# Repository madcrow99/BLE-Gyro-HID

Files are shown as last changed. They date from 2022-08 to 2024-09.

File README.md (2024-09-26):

# BLE-Gyro-HID

This project is to create a low-cost human interface device (HID) that enables people with motor impairments to control phones and computers. Basically, a mouse that requires very limited head movements to operate.
please see this repository for how to game and control phones using only eye gaze https://github.com/madcrow99/windows-eye-control-of-external-devices.git

The device uses a gyroscope mounted to an earpiece to track head movements (very little movement required) and move a mouse pointer accordingly. The device has 4 optional switch / button inputs (3.5mm headphone jack) for use with any switches that the user can control.

left: works the same as the left click button on a regular mouse

right: works the same as the right click button on a regular mouse 

scroll: tap to scroll down and long press to scroll up

dwell: tap to to toggle dwell clicking on and off. Dwell clicking is where the device will left click/tap when the pointer is stationary for a specified time. Being able to turn this feature on and off really helps the user from going crazy when the mouse constantly clicks.





The device uses an Adafruit Feather Express nRF52840 and an IMU module to act as a Bluetooth low energy mouse. Please see the bill of materials for details. The case and gyro cover are 3d printed. The STL and STEP files ae included. The Nordic nRF52840 is an amazing device and the Adafruit implementation of it is awesome. Thanks Adafruit for the wonderfully easy to use libraries!

An instruction manual for building the device is included.

The software has to be uploaded to the nRF52840. Platformio is recommended. Here is a link to the setup instructions:
https://platformio.org/install/ide?install=vscode

An Android App that performs swipe gestures when clicked can be found here
https://github.com/madcrow99/AndroidMousePointerSwipeGestures
This is quite helpful for navigating an android device while dwell cicking.

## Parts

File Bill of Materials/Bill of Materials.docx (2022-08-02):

Bill of Materials

The majority of the parts come from Adafruit:

https://www.adafruit.com/

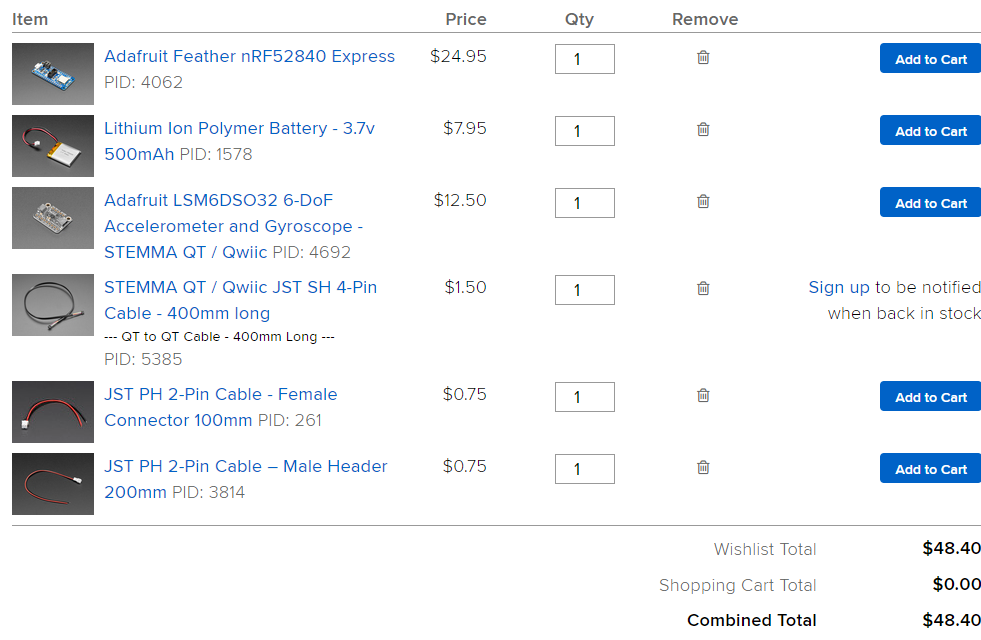
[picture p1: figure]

The parts below are from Amazon but can be purchased elsewhere. Digikey is a great source.

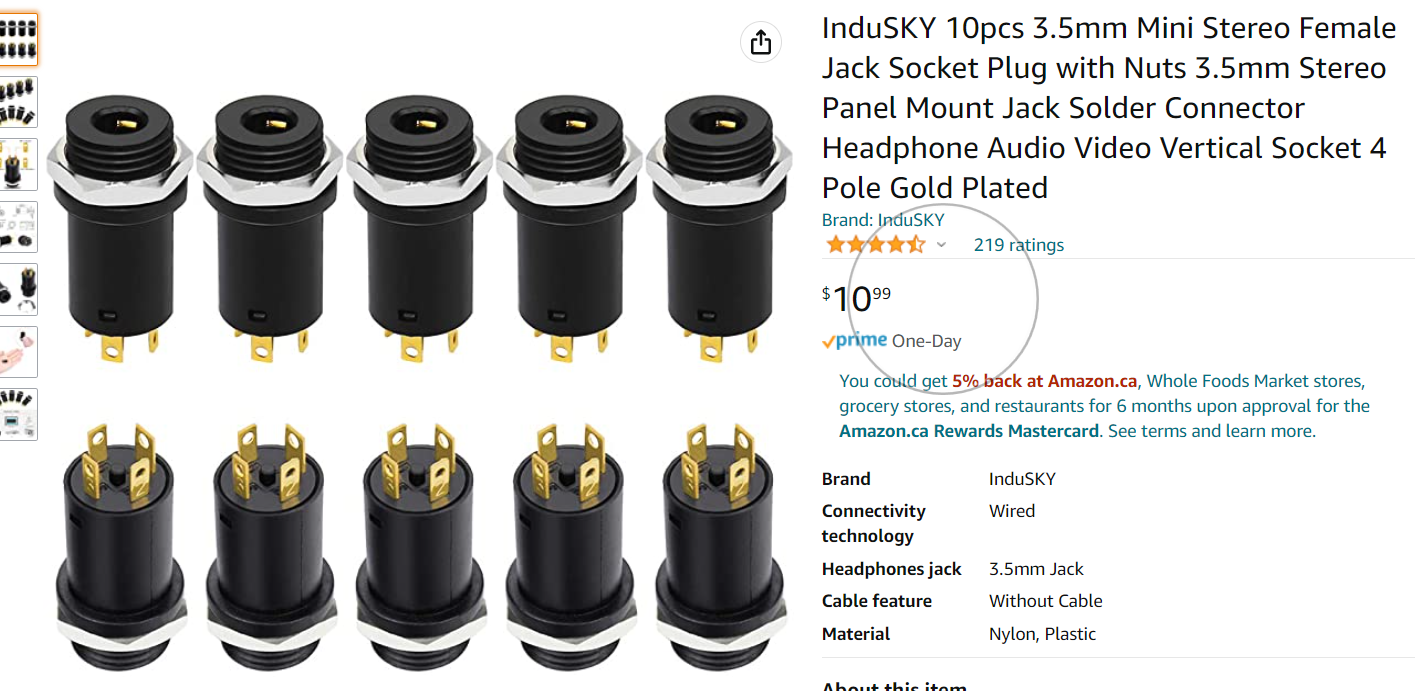
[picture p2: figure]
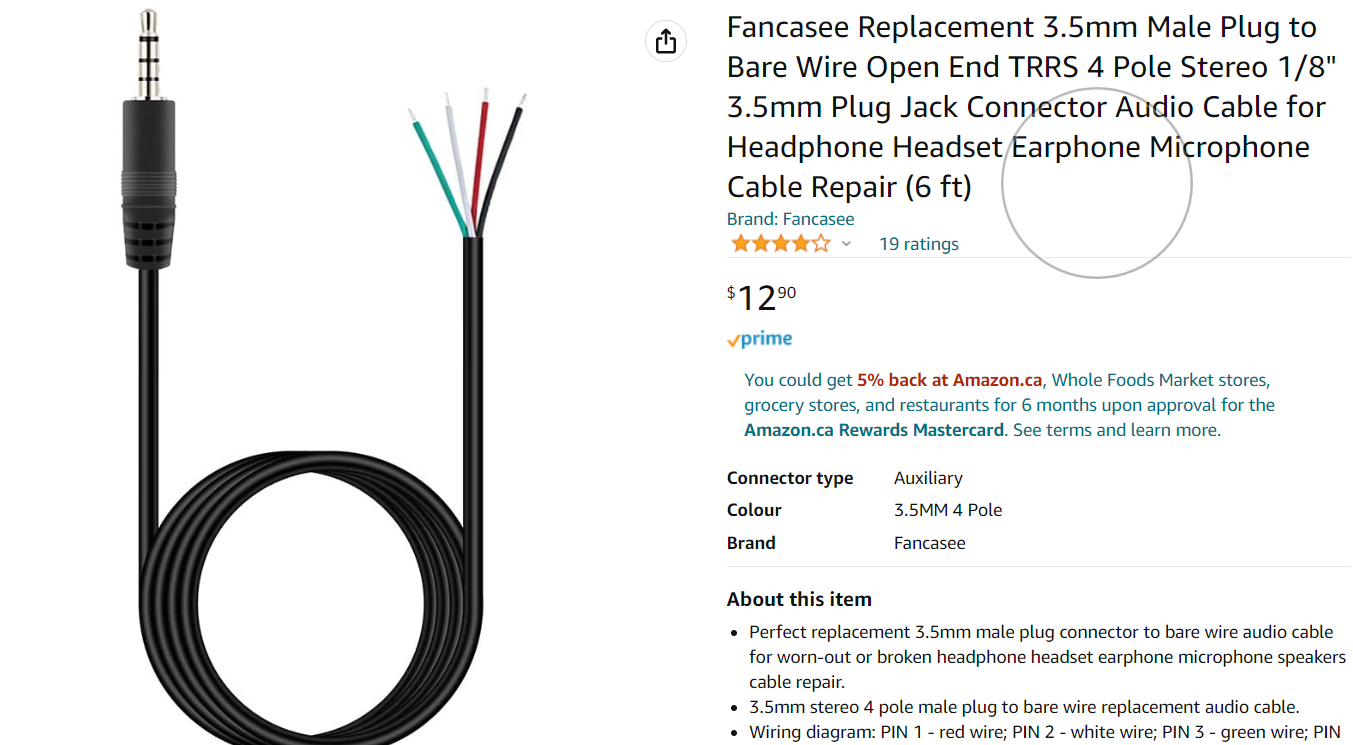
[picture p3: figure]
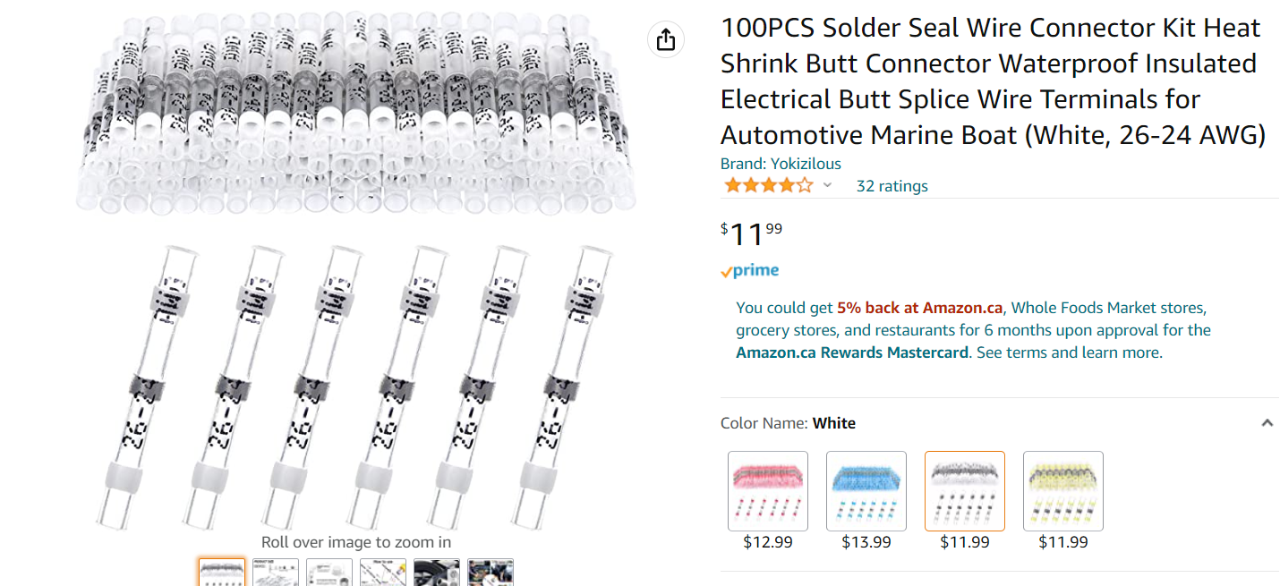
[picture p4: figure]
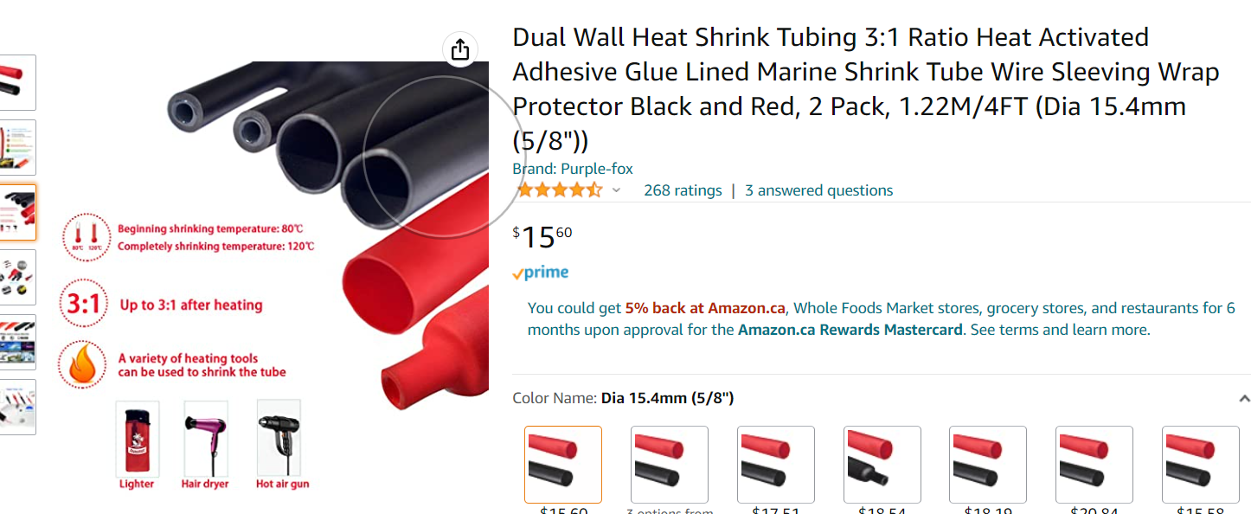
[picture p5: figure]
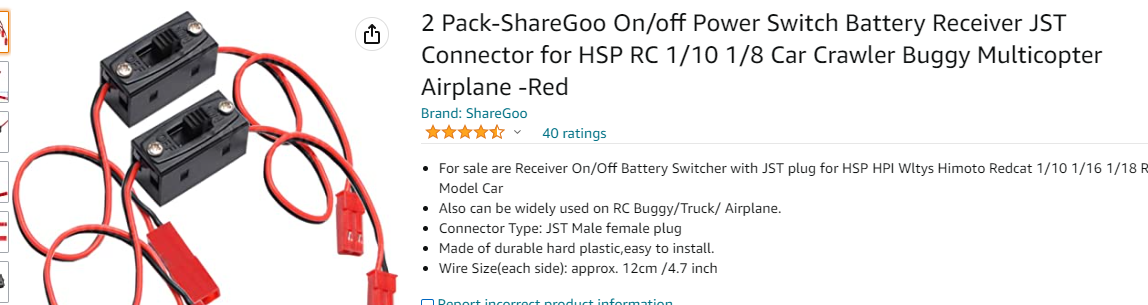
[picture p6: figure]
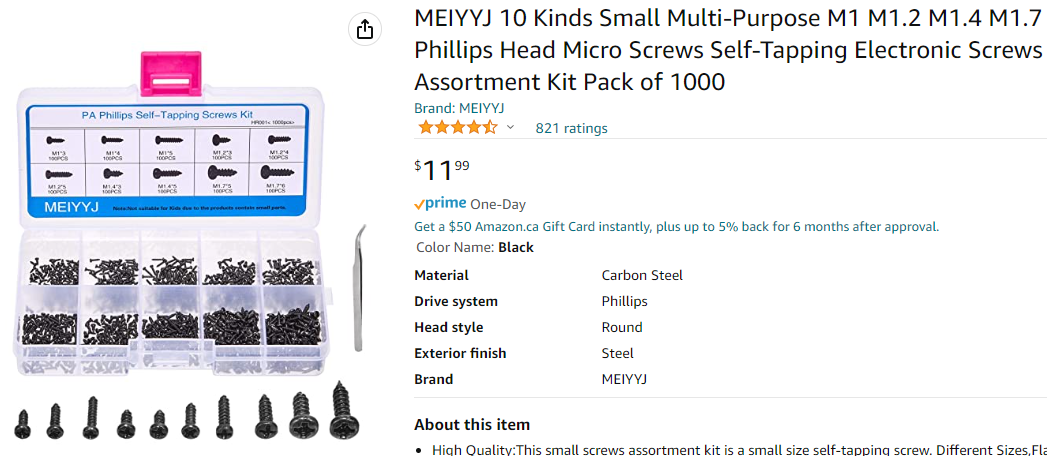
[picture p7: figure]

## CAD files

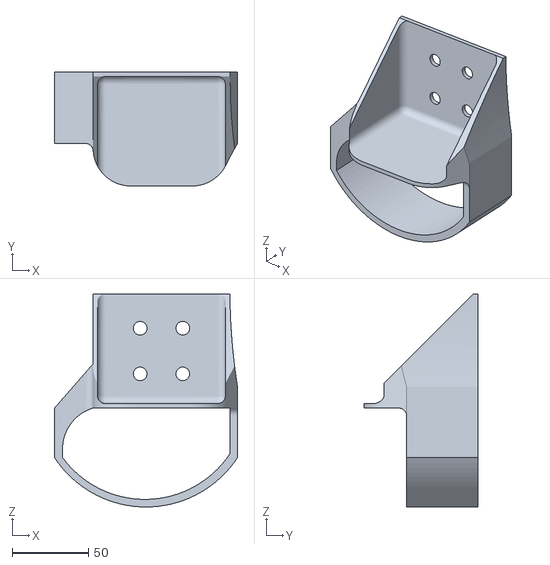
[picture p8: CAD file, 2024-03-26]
3D print STL files/Hand Button Mount Left.stl
120.3 x 75.0 x 140.0

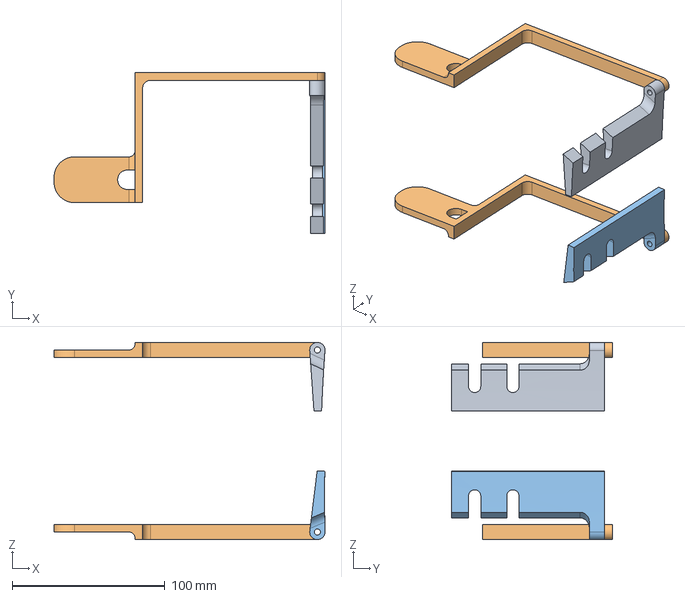
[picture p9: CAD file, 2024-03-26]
CAD STEP Files/Head Button Mount.step
177.2 x 105.0 x 129.0 mm

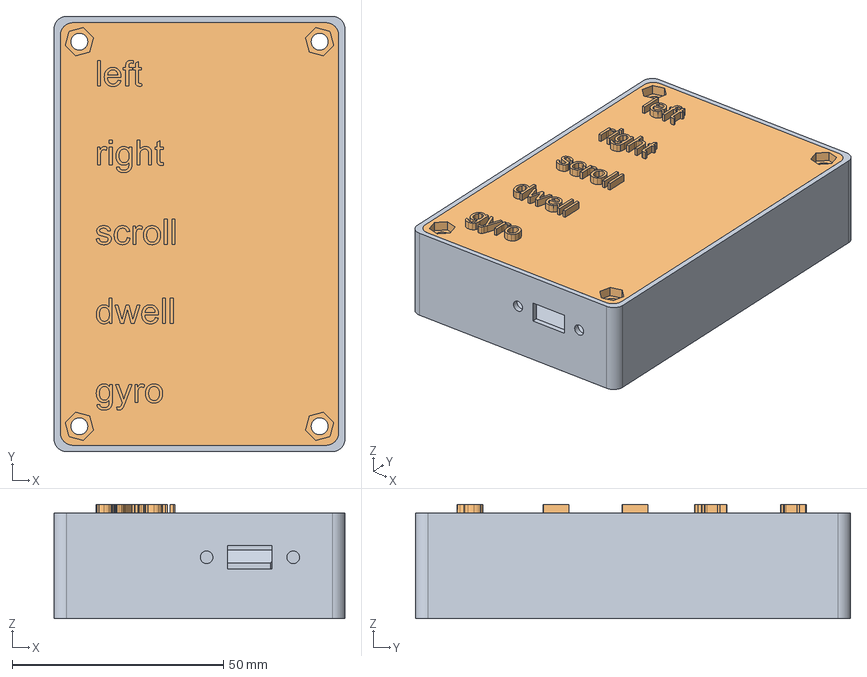
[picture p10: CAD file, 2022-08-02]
CAD STEP Files/HID Case.step
68.9 x 103.0 x 27.0 mm
case
lid

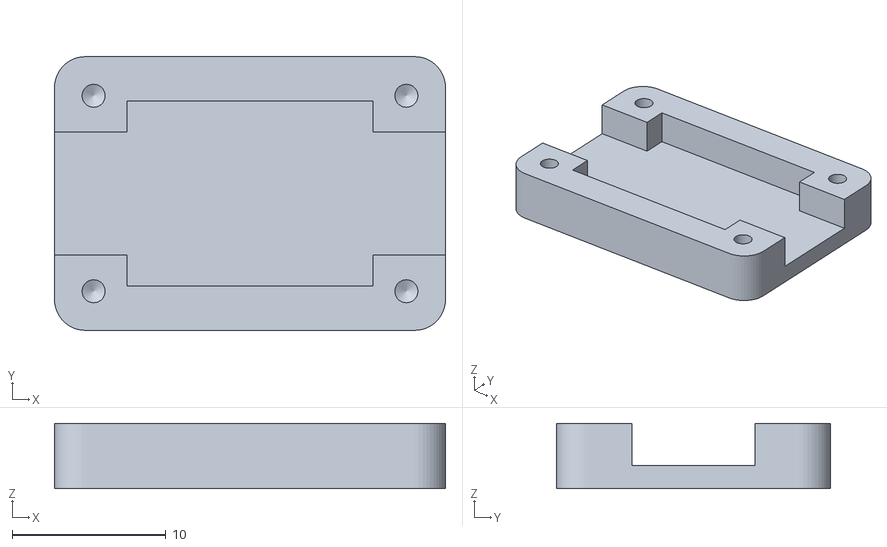
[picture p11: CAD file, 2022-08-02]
3D print STL files/gyro cover.stl
25.4 x 17.8 x 4.25

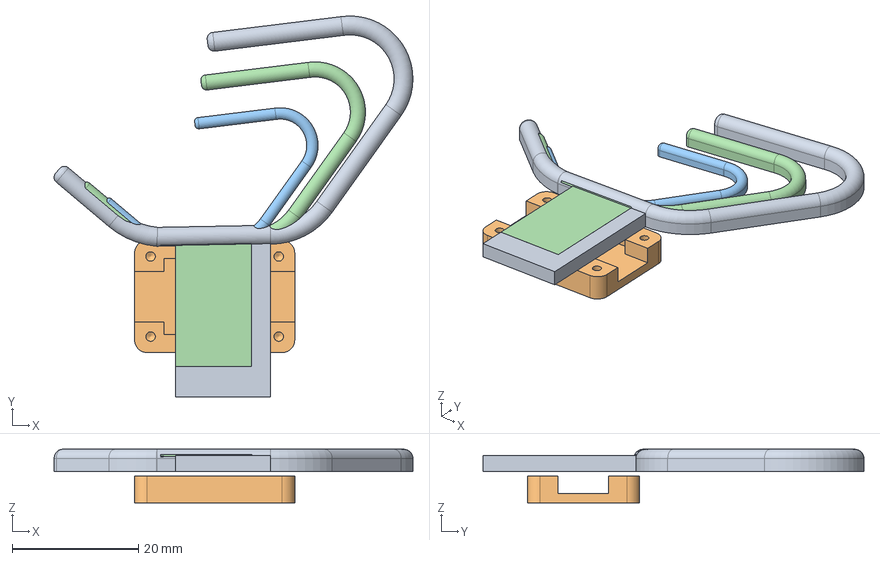
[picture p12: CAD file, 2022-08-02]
CAD STEP Files/HID earpiece.step
56.9 x 60.4 x 8.50 mm
earpiece large
gyro cover
earpiece small
earpiece_1

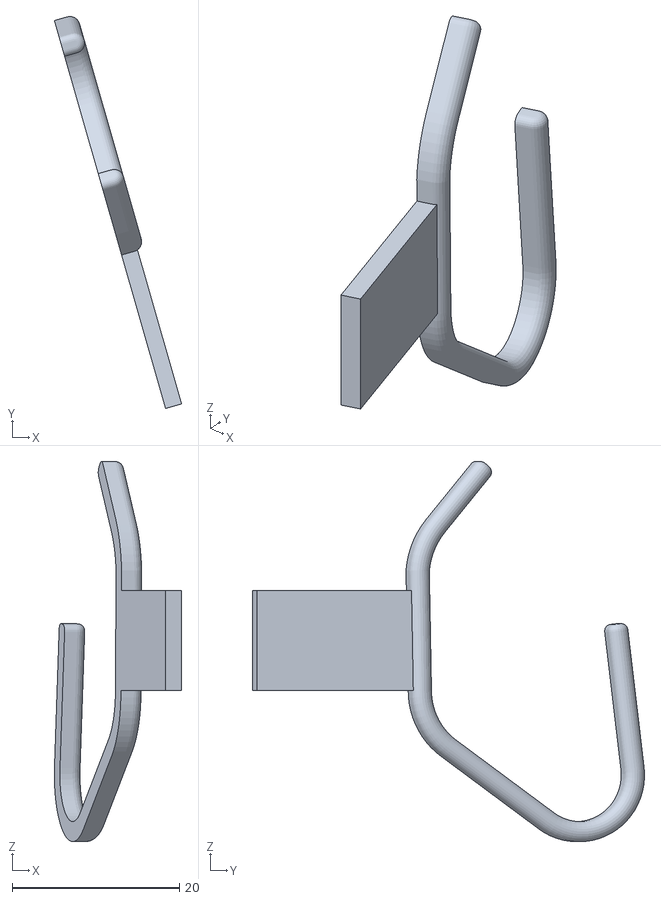
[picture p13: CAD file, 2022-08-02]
3D print STL files/earpiece.stl
15.2 x 46.9 x 45.5

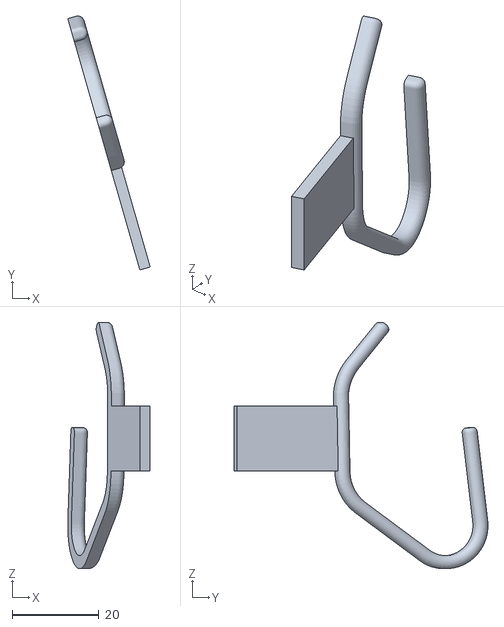
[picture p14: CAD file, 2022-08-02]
3D print STL files/earpiece large.stl
19.1 x 58.7 x 56.9

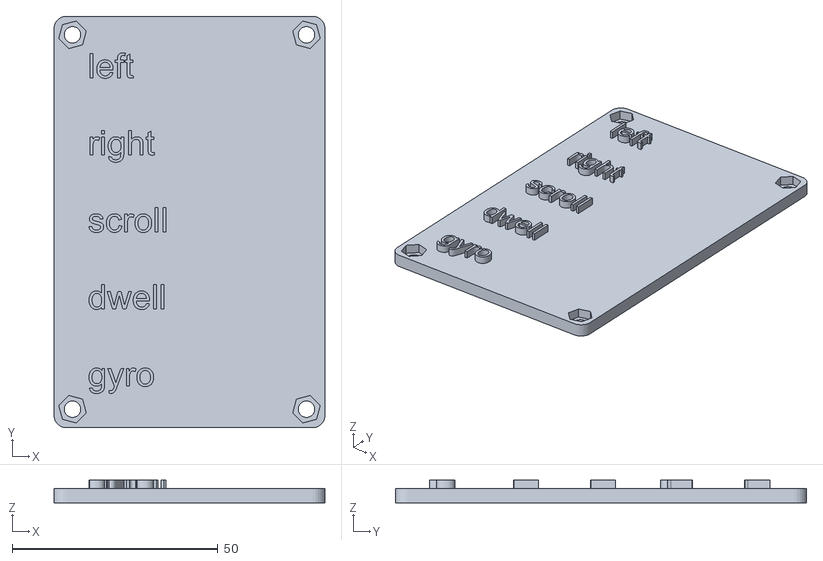
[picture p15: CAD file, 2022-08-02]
3D print STL files/lid.stl
65.9 x 100.0 x 5.50

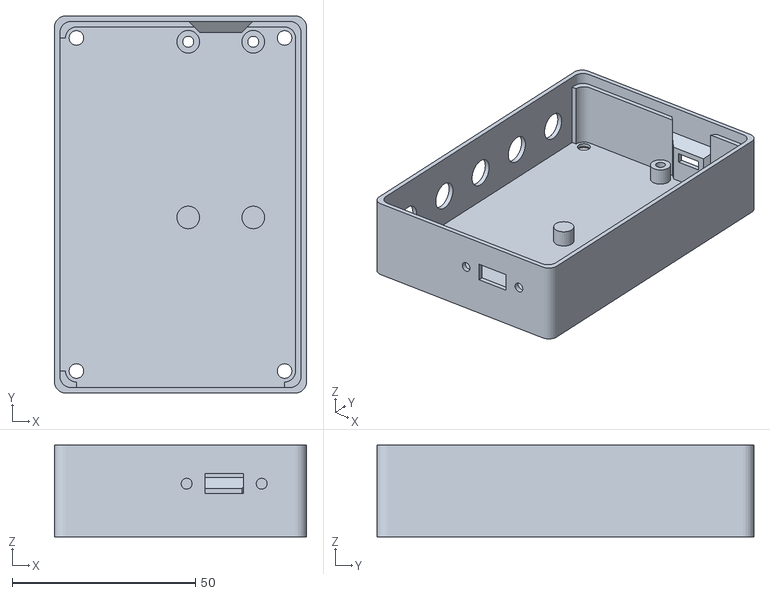
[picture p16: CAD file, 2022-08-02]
3D print STL files/case.stl
68.9 x 103.0 x 25.0

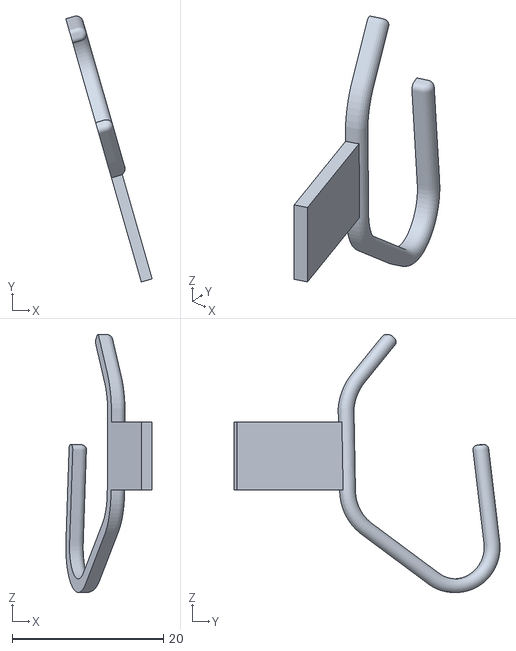
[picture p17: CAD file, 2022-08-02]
3D print STL files/earpiece small.stl
11.4 x 35.2 x 34.1

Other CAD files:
3D print STL files/Hand Button Mount Right.stl
3D print STL files/Head Button Mount.stl

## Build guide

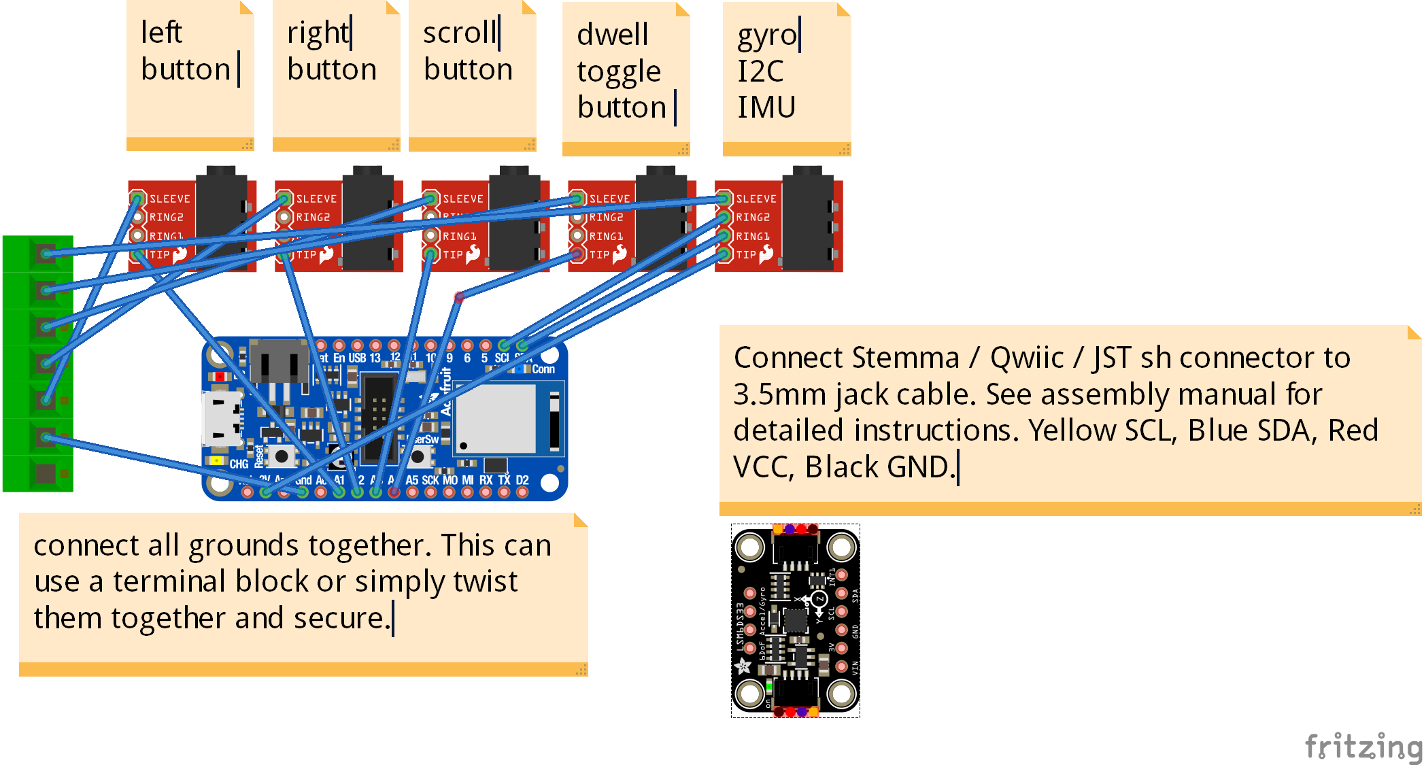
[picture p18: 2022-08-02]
Wiring Diagram/gyro HID Sketch_bb.png

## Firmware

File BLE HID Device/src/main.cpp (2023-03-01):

// need to add license
#include <Arduino.h>
#include <bluefruit.h>
#include <Adafruit_LSM6DSOX.h>
#include <Bounce2.h>
#include <array>

BLEDis bledis;
BLEHidAdafruit blehid;

boolean gyro_connected = false;

Adafruit_LSM6DSOX sox;
sensors_event_t accel;
sensors_event_t gyro;
sensors_event_t temp;

const double averageX = -0.013; // gyro drift compensation
const double averageY = 0;
const double averageZ = 0.013;
int8_t gx, gy; // calculated mouse movement from gyro sensor

const int NUM_BUTTONS = 4;
Bounce *buttons = new Bounce[NUM_BUTTONS]; // set up 4 buttons with denouncing(left click, right click, scroll, dwell click toggle)
int BUTTON_PINS[NUM_BUTTONS] = {A2, A3, A4, A5};

// mouse control options
boolean dwell = false;
boolean dwellActive = false;
unsigned long dwellTimer;
unsigned long dwellLength = 650;

bool button_active[NUM_BUTTONS] = {false, false, false, false};
bool long_press_active[NUM_BUTTONS] = {false, false, false, false};
unsigned long button_timer[4];
unsigned long long_press_time[4] = {1000000, 100000, 500, 1000000};
int8_t click_action[4][4] = {{1, 0, 0, 0}, {2, 0, 0, 0}, {0, 0, 0, 0}, {0, 0, 0, 0}}; // for mousereport function: button, x, y, scroll
// short_click_action and long_click_action are for buttons that act differently on short vs long press. Scroll button in our case
int8_t short_click_action[4][4] = {{0, 0, 0, 0}, {0, 0, 0, 0}, {0, 0, 0, -5}, {0, 0, 0, 0}}; // for short press mousereport function: button, x, y, scroll
int8_t long_click_action[4][4] = {{0, 0, 0, 0}, {0, 0, 0, 0}, {0, 0, 0, 1}, {0, 0, 0, 0}};   // for long press mousereport function: button, x, y, scroll

// header functions located after setup and loop functions
void dwell_click_control();
void mouse_click_control();
void startAdv(void);

void setup()
{

  Serial.begin(115200);
  Bluefruit.begin();
  // HID Device can have a min connection interval of 9*1.25 = 11.25 ms
  Bluefruit.Periph.setConnInterval(9, 16); // min = 9*1.25=11.25 ms, max = 16*1.25=20ms
  Bluefruit.setTxPower(4);                 // Check bluefruit.h for supported values
  // Bluefruit.setName("ICAN HID Device");
  Bluefruit.setName("ICAN HID Device");

  // Configure and Start Device Information Service
  bledis.setManufacturer("Adafruit Industries");
  bledis.setModel("Bluefruit Feather 52");
  bledis.begin();

  // BLE HID
  blehid.begin();

  // Set up and start advertising
  startAdv();

  if (!sox.begin_I2C())
  {
    Serial.println("Failed to find IMU chip");
  }
  else
    gyro_connected = true;

  for (int i = 0; i < NUM_BUTTONS; i++)
  {
    buttons[i].attach(BUTTON_PINS[i], INPUT_PULLUP); // setup the bounce instance for the current button
    buttons[i].interval(30);                         // interval in ms
  }
}

void loop()
{

  if (gyro_connected == true)
  {
    // Get a new normalized sensor event
    sox.getEvent(&accel, &gyro, &temp);

    gx = -((gyro.gyro.x - averageX) / 0.03); // change value as needed for mouse sensitivity
    gy = -((gyro.gyro.z - averageZ) / 0.03); // change value as needed for mouse sensitivity
    if (gx != 0 || gy != 0)
    {
      blehid.mouseMove(gx * 10, gy * 10); // change value as needed for mouse sensitivity
    }

    delay(5); // adjust the delay for smooth pointer movement
  }
  for (int i = 0; i < NUM_BUTTONS; i++)
  {
    // Update button state after debouncing
    buttons[i].update();
  }
  // check if dwell click has been toggled on and click if appropriate
  if (dwell && gyro_connected == true)
    dwell_click_control();
  // check for left, right scroll and dwell toggle and perform appropriate action
  mouse_click_control();
}

void dwell_click_control()
{ // check if pointer has met movement and time conditions and that the scroll button isn't pressed
  if (-1 <= gx && gx <= 1 && -1 <= gy && gy <= 1 && buttons[3].read() == HIGH)
  {
    if (dwellActive == false)
    {
      dwellActive = true;
      dwellTimer = millis();
    }
    if ((millis() - dwellTimer > dwellLength))
    {
      blehid.mouseButtonPress(1); // left click
      delay(50);                  // this delay can be adjusted if the click is not responding appropriately
      blehid.mouseButtonRelease();
      dwellActive = false;
    }
  }
  else
  {
    dwellActive = false;
  }
  mouse_click_control();
}

void mouse_click_control()
{

  for (int i = 0; i < NUM_BUTTONS; i++)
  {
    if (buttons[i].read() == LOW)
    {
      if (button_active[i] == false)
      {
        button_active[i] = true;
        button_timer[i] = millis();
        // press left or right button and start timing the press for scroll button
        blehid.mouseReport(click_action[i][0], click_action[i][1],
                           click_action[i][2], click_action[i][3]);

        Serial.println(i);
      }
      if (millis() - button_timer[i] > long_press_time[i])
      {
        long_press_active[i] = true;
        blehid.mouseReport(long_click_action[i][0], long_click_action[i][1],
                           long_click_action[i][2], long_click_action[i][3]);
      }
    }
    else if (buttons[i].read() == HIGH)
    { // button is not pressed
      if (button_active[i] == true)
      { // button was pressed in the prior loop
        if (long_press_active[i] == true)
        {                               // button was long pressed in prior loop
          long_press_active[i] = false; // set long press activated to false(i.e. Reset)
        }
        else
        { // execute short button press action
          if (i != 3)
          { // not the dwell click toggle switch
            blehid.mouseReport(short_click_action[i][0], short_click_action[i][1],
                               short_click_action[i][2], short_click_action[i][3]);
          }
          else
            dwell = !dwell; // togge dwell click or off
          Serial.println("dwell");
        }
      }
      button_active[i] = false;
    }
  }
}

void startAdv(void)
{
  // Advertising packet
  Bluefruit.Advertising.addFlags(BLE_GAP_ADV_FLAGS_LE_ONLY_GENERAL_DISC_MODE);
  Bluefruit.Advertising.addTxPower();
  Bluefruit.Advertising.addAppearance(BLE_APPEARANCE_HID_MOUSE);

  // Include BLE HID service
  Bluefruit.Advertising.addService(blehid);

  // There is enough room for 'Name' in the advertising packet
  Bluefruit.Advertising.addName();

  /* Start Advertising
   * - Enable auto advertising if disconnected
   * - Interval:  fast mode = 20 ms, slow mode = 152.5 ms
   * - Timeout for fast mode is 30 seconds
   * - Start(timeout) with timeout = 0 will advertise forever (until connected)
   *
   * For recommended advertising interval
   * https://developer.apple.com/library/content/qa/qa1931/_index.html
   */
  Bluefruit.Advertising.restartOnDisconnect(true);
  Bluefruit.Advertising.setInterval(32, 244); // in unit of 0.625 ms
  Bluefruit.Advertising.setFastTimeout(30);   // number of seconds in fast mode
  Bluefruit.Advertising.start(0);             // 0 = Don't stop advertising after n seconds
}

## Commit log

2022-06-20 Add files via upload
    added pen and paper wiring schematic
2022-08-02 added a check for gyro attached
2023-03-01 fixed Brackets in line 90
